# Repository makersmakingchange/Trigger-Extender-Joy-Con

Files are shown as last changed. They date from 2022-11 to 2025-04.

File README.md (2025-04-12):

# Trigger Extenders for Joy-Con Controller
The Trigger Extenders for Joy-Con Controllerr is an aid designed to make it easier to use the triggers and bumpers on the Nintendo Joy-Con controller.

Picture of Trigger Extender for Joy-Con.

## More info at
- [Makers Making Change Project Page](https://makersmakingchange.com/project/trigger-extender-joy-con/)

## How to Obtain a Trigger Extenders for Joy-Con
### 1. Do it Yourself (DIY) or Do it Together (DIT)

This is an open-source assistive technology, so anyone is free to build it. All of the files and instructions required to build the Trigger Extenders for Joy-Con are contained within this repository. Refer to the Maker Checklist below.

### 2. Request a build of this device

If you would like to obtain a Trigger Extenders for Joy-Con, you may submit a build request through the [MMC Library Page](https://makersmakingchange.com/project/trigger-extender-joy-con/). The requestor is responsible for the cost of materials and any shipping.

### 3. How to build this device for someone else

If you have the skills and equipment to build this device, and would like to donate your time to create it for someone who needs it, visit the [MMC Maker Wanted](https://makersmakingchange.com/maker-wanted/) section.

## Getting Started

### 1. Read the Makers Checklist

The Makers Checklist provides an overview of the steps required to build the device.

### 2. Print the 3D Printable components

Print the components. Refer to the 3D Printing Guide.

All of the files and individual print files can be in the [/Build_Files/3D_Printing_Files](/Build_Files/3D_Printing_Files/) folder.

### 3. Assemble the Trigger Extenders for Joy-Con

Reference the [Assembly Guide](/Documentation/Trigger_Extender_Joycon_Assembly_Guide_V1.0.pdf) for the tools and steps required to build each portion.

## Files
### Documentation
| Document             | Version | Link |
|----------------------|---------|------|
| Design Rationale     | 1.0     | [Trigger_Extender_Joycon_Design_Rationale](/Documentation/Trigger_Extender_Joycon_Design_Rationale_V1.0.pdf)     |
| Maker Checklist      | 1.0     | [Trigger_Extender_Joycon_Maker_Checklist](/Documentation/Trigger_Extender_Joycon_Maker_Checklist_V1.0.pdf)     |
| Bill of Materials    | 1.0     | [Trigger_Extender_Joycon_Bill_of_Materials](/Documentation/Trigger_Extender_Joycon_BOM_V1.0.xlsx)     |
| 3D Printing Guide    | 1.0     | [Trigger_Extender_Joycon_3D_Printing_Guide](/Documentation/Trigger_Extender_Joycon_3D_Printing_Guide_V1.0.pdf)     |
| Assembly Guide       | 1.0     | [Trigger_Extender_Joycon_Assembly_Guide](/Documentation/Trigger_Extender_Joycon_Assembly_Guide_V1.0.pdf)     |
| User Guide           | 1.0     | [Trigger_Extender_Joycon_User_Guide](/Documentation/Trigger_Extender_Joycon_User_Guide_V1.0.pdf)    |
| Changelog            | 1.0     | [Trigger_Extender_Joycon_Changelog](/Documentation/Trigger_Extender_Joycon_Changelog_V1.0.pdf)     |

### Build Files
 - [3D Printing Files](/Build_Files/3D_Printing_Files/)

## Attribution
Designer:
 - Sacha Potvin in the [GRRIT Program](https://albertahealthservices.ca/grh/Page14207.aspx) of the Glenrose Rehabilitation Hospital
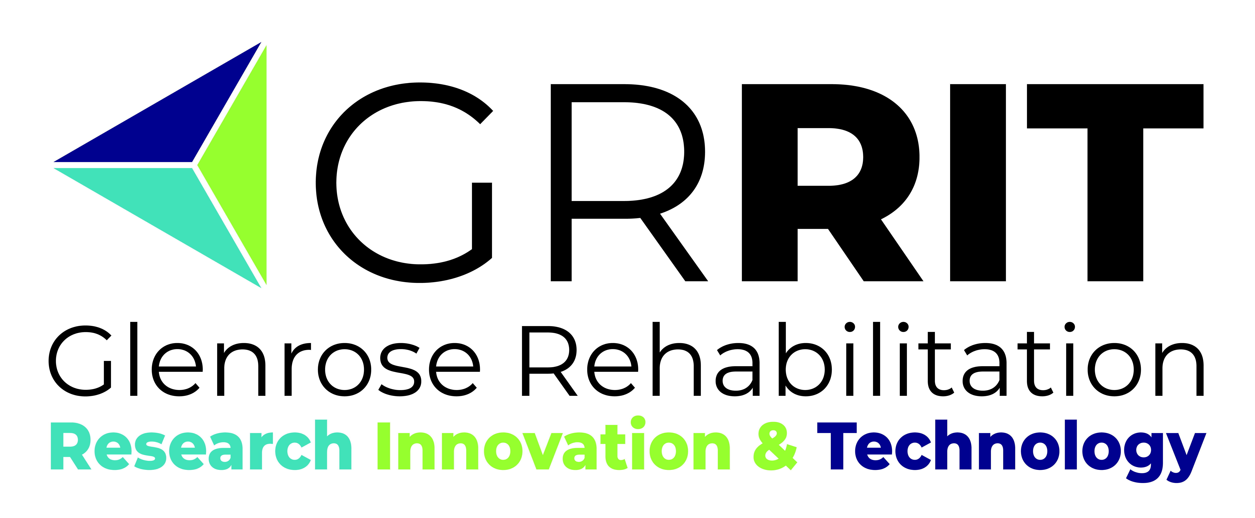
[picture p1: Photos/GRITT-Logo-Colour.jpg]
GRRIT Logo.


Documentation: 
 - Makers Making Change

## License
Everything needed or used to design, make, test, or prepare the Trigger Extenders for Joy-Con is licensed under the CERN 2.0 Permissive license <https://ohwr.org/project/cernohl/wikis/Documents/CERN-OHL-version-2> (CERN-OHL-P) . 

Accompanying material such as instruction manuals, videos, and other copyrightable works that are useful but not necessary to design, make, test, or prepare the Trigger Extenders for Joy-Con are published under a Creative Commons Attribution-ShareAlike 4.0 license https://creativecommons.org/licenses/by-sa/4.0/ (CC BY-SA 4.0).

---
<!-- ABOUT MMC START -->
## About Makers Making Change
[Makers Making Change Logo](https://www.makersmakingchange.com/)

Makers Making Change is a program of [Neil Squire](https://www.neilsquire.ca/), a Canadian non-profit that uses technology, knowledge, and passion to empower people with disabilities.

Makers Making Change leverages the capacity of community based Makers, Disability Professionals and Volunteers to develop and deliver affordable Open Source Assistive Technologies.

 - Website: [www.MakersMakingChange.com](https://www.makersmakingchange.com/)
 - GitHub: [makersmakingchange](https://github.com/makersmakingchange)
 - Bluesky: [@makersmakingchange.bsky.social](https://bsky.app/profile/makersmakingchange.bsky.social)
 - Instagram: [@makersmakingchange](https://www.instagram.com/makersmakingchange)
 - Facebook: [makersmakechange](https://www.facebook.com/makersmakechange)
 - LinkedIn: [Neil Squire Society](https://www.linkedin.com/company/neil-squire-society/)
 - Thingiverse: [makersmakingchange](https://www.thingiverse.com/makersmakingchange/about)
 - Printables: [MakersMakingChange](https://www.printables.com/@MakersMakingChange)

### Contact Us
For technical questions, to get involved, or to share your experience we encourage you to [visit our website](https://www.makersmakingchange.com/) or [contact us](https://www.makersmakingchange.com/s/contact).
<!-- ABOUT MMC END -->

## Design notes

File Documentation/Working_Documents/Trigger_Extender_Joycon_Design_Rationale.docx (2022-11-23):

# Introduction

The Trigger Extenders for Joy-Con Controller is designed to extend the shoulder bumpers and triggers on the Nintendo Joy-Con Controller to make it easier to activate them.

The device is intended for users that have issues using the shoulder bumpers and triggers on the Nintendo Joy-Con Controller.

# Research

No similar commercial or DIY products could be found.

# Requirements

## Goals

G01 | Extend the shoulder bumpers and triggers so they can be activated from more positions

## Functional Requirements

F01 | Device must extend the bumpers to be activated from more locations
F02 | Device must extend the triggers to be activated from more locations
F03 | Device must be easily attached and removed from the Nintendo Joy-Con Grip

## Constraints

C01 | Device must be entirely 3D printed

# Testing

The parts were printed, and the extenders were attached and removed from the slide-on trigger attachment 50 times to see if they would hold up over time. At the end of the testing the parts still work, although the attachments are slightly looser.

# Detailed Design

## Slide-on Trigger Attachment

~110x30x20mm

## Shoulder Trigger Extender

~160x35x5mm

## Shoulder Bumper Extender

~140x40x5mm

# Opportunities for Improvement

- The trigger extenders can break after repeatedly attaching and being removed from the trigger attachment. However, they need to be removed to take the Joy-Cons out to charge and use with the main switch body. Redesigning the extender so that it doesn’t block the insertion and removal of the Joy-Cons would extend the lifespan of this device.

© 2022 by Neil Squire. This work is licensed under the CC BY SA 4.0 License: http://creativecommons.org/licenses/by-sa/4.0 Files available at https://makersmakingchange.com/project/trigger-extender-joy-con/ Page 1 of 1

V1.0 | October 2022 Trigger Extenders for Joy-Con Controller Design Rationale

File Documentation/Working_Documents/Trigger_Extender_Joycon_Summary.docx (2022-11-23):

# Title

Trigger Extenders for Joy-Con Controller

## Subtitle

The Trigger Extender for Joy-Con Controller is an aid designed to make it easier to use the triggers and bumpers on the Nintendo Joy-Con Controller Grip.

## Device Details

### Overview

This 3D printed device attaches to the Nintendo Joy-Con Grip and extends the trigger and bumper buttons users to use the buttons more easily. The extenders allow for the bumper and trigger buttons to be activate from more positions.

### Usage

After assembling the device, the extenders can be pressed anywhere along their front to activate their respective button.

### Cost

~$0.50 for filament

### Build Instructions

To use this device, attach the central Slide-On Trigger Attachment to the centre of the Joy-Con Grip. Next insert the Joy-Cons to the Grip, then insert the trigger extenders in the lower clip and the bumper extenders in the upper clip.

#### Skills Required

- 3D Printing

#### Time Required

Printing time: 3h 1min

Assembly time: <5min

#### Tools

- 3D Printer

#### Components

- Slide-on Trigger Attachment
- Shoulder Trigger Extender
- Shoulder Bumper Extender

#### 3D Printing

All components can be printed with no support at 20% infill with a 0.2 layer height. All pieces can be printed using PLA filament.

### Attribution

Design: Sacha Potvin in the GRRIT Program (https://albertahealthservices.ca/grh/Page14207.aspx) of the Glenrose Rehabilitation Hospital

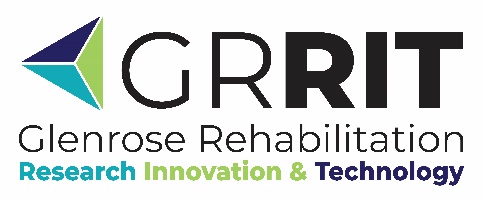
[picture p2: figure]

Documentation: Neil Squire / Makers Making Change

© 2022 by Neil Squire. This work is licensed under the CC BY SA 4.0 License: http://creativecommons.org/licenses/by-sa/4.0 Files available at https://makersmakingchange.com/project/trigger-extender-joy-con/ Page 1 of 2

V1.0 | October 2022 Trigger Extenders for Joy-Con Controller Summary

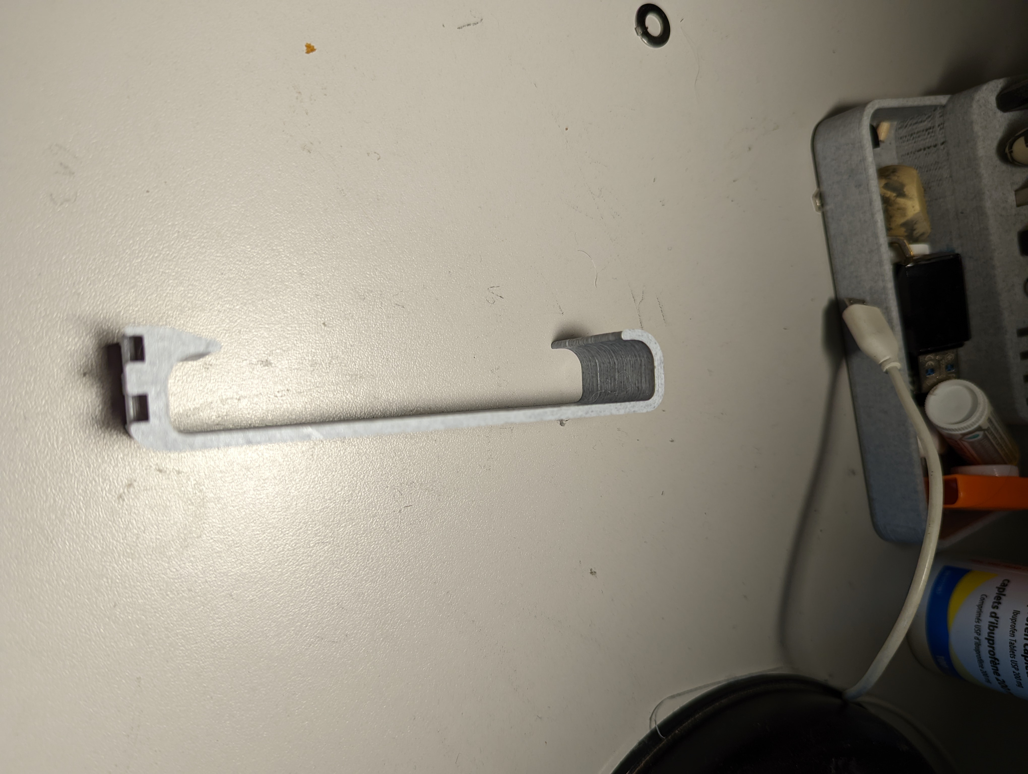
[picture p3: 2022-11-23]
Photos/Slide-On Trigger Attachment Side View.jpg

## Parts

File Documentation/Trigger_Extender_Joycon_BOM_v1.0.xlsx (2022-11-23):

Trigger Extenders for Joy-Con |  | Total Cost | Total Print time (hr) | Total filament (g)
Version: V1.0 | Last Updated: 2022-Nov-21 | $0.50 | 3.02 | 20
Commercial Parts:
Part type (Electrical. Mechanical, Sanitization, ect) | Part Name | Quantity Needed | Pkg Quantity | Price per package | Price per Unit | Price for qty needed | Link
N/A
3D Printed Parts ESTIMATED PRICING USING 1KG ROLL COST: | $25.00
Part | Description | Quantity Needed | TOTAL Mass (g) | Estimated Price | Print Time (Min) | Link
Slide-on Trigger Attachment | Attachment point for both extenders | 1 | 11 | $0.27 | 98
Shoulder Trigger Extender | Extender for the trigger buttons | 1 | 5 | $0.12 | 43
Shoulder Bumper Extender | Extender for the shoulder buttons | 1 | 4 | $0.10 | 40
 |  |  |  | $0.00
 |  |  |  | $0.00
 |  |  | Total Print Cost: | $0.50
Tools for Assembly
None required.
Alternatives (if there are other sources for some parts link them below)
Part and description | Link

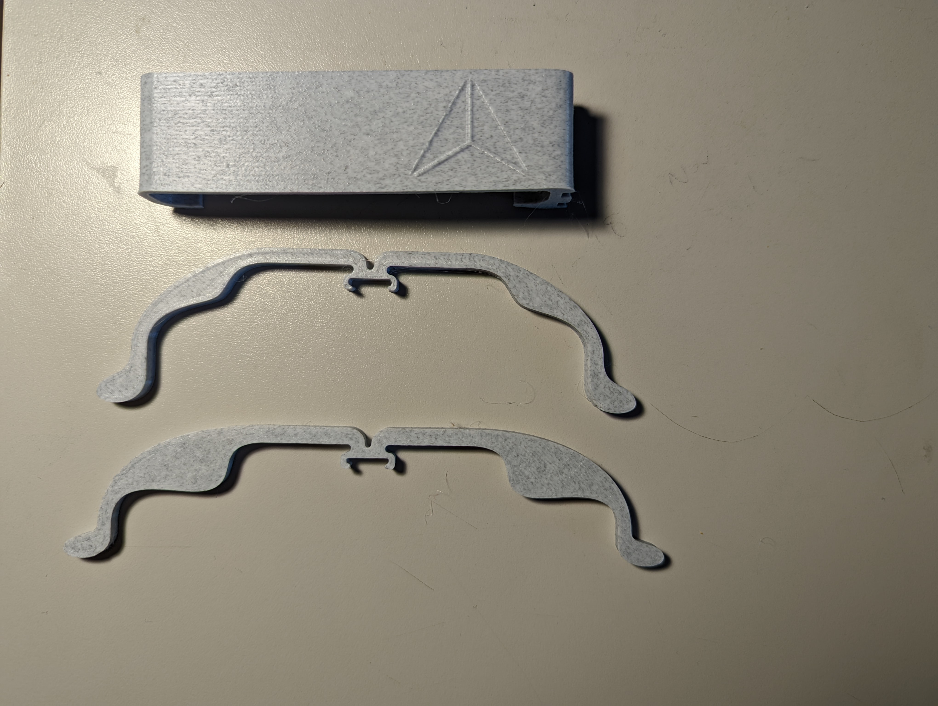
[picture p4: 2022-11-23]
Photos/All-Components-Top-View.jpg

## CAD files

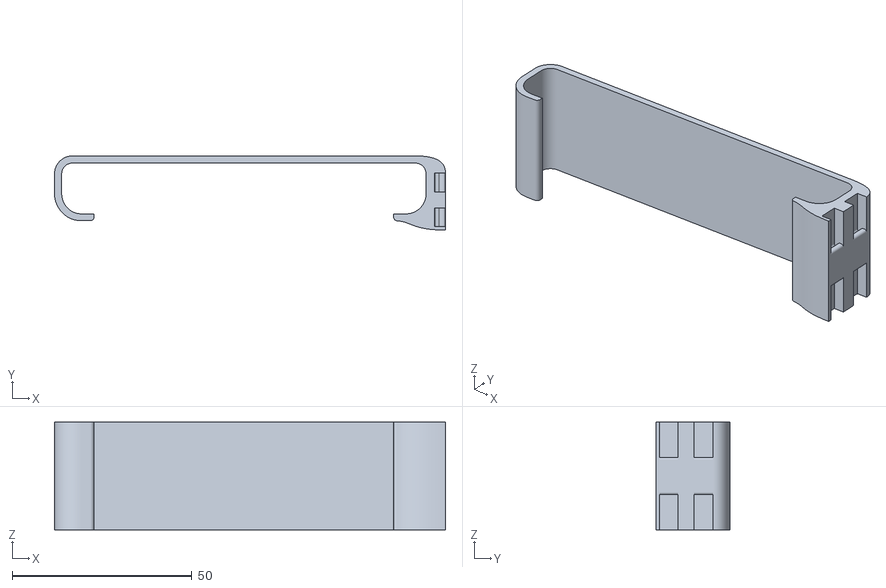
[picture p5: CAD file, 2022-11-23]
Build_Files/3D_Printing_Files/Slide-on Trigger Attachment.STL
108.6 x 20.6 x 30.0

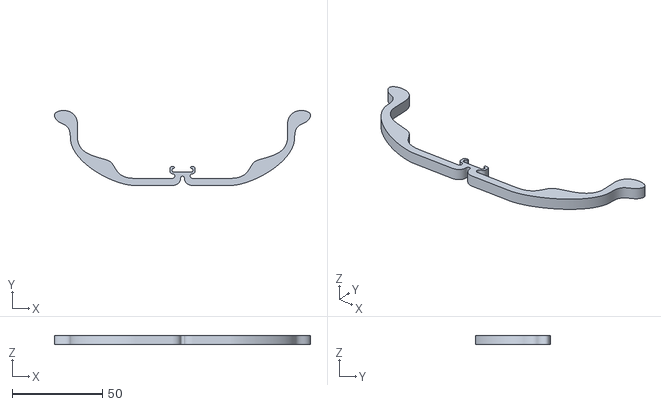
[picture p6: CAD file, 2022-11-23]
Build_Files/3D_Printing_Files/Shoulder Bumper Extender.STL
142.2 x 41.7 x 5.18

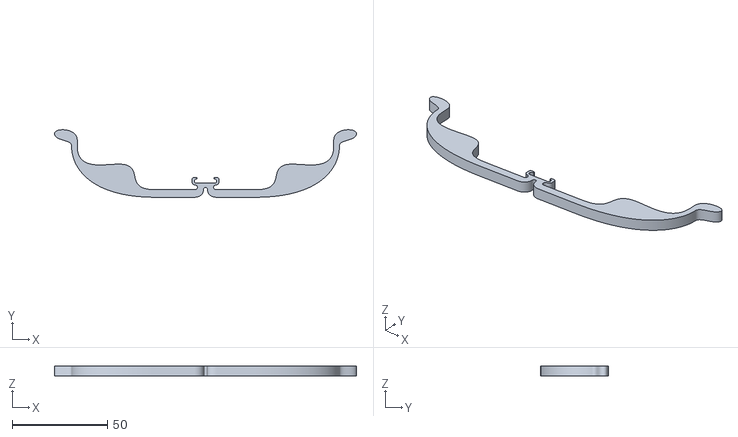
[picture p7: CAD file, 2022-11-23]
Build_Files/3D_Printing_Files/Shoulder Trigger Extender.STL
158.1 x 35.4 x 5.00

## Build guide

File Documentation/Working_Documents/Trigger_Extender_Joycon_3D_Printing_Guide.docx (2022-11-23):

# 3D Printing Summary

Metrics | V1.0
Total Print Time (min) | 181
Total Number of Components | 3
Typical Total Mass (g) | 20
Typical Number of Print Setups | 1

# 3D Printing Settings

Print File Name | Qty | Total Print Time (hr:min) | Mass (g) | Infill (%) | Support(Y/N) | Layer Height/ Nozzle Diameter(mm) | Notes (orientation, special settings, etc.)
Slide-on Trigger Attachment.stl | 1 | 1:38 | 11 | 20 | N | 0.2/0.4 | - Print in default STL orientation
Shoulder Trigger Extender.stl | 1 | 0:43 | 5 | 20 | N | 0.2/0.4 | - Print in default STL orientation
Shoulder Bumper Extender.stl | 1 | 0:40 | 4 | 20 | N | 0.2/0.4 | - Print in default STL orientation

# Customization Options

- Any of the 3 parts can be printed in separate colours to customize the Trigger Extenders

# Post-Processing

- Any sharp edges should be sanded down/filed off.

# Examples of Quality Prints

Photos of Slide-on Trigger Attachment.stl

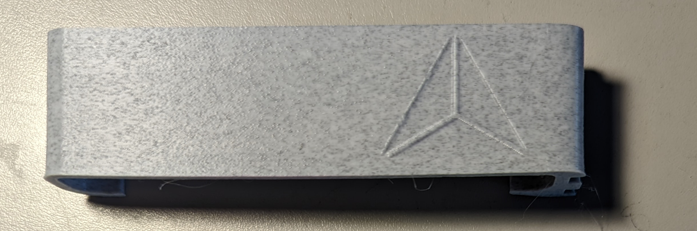
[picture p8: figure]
Trigger Attachment top view
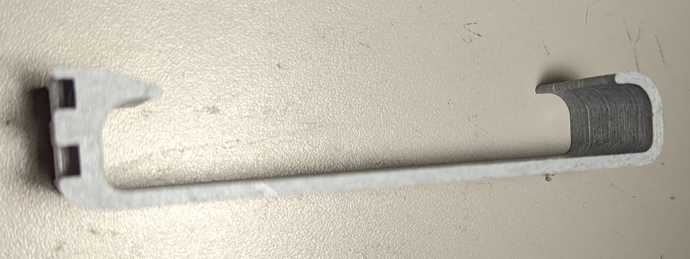
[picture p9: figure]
Trigger Attachment side view

Photos of Shoulder Trigger Extender.stl

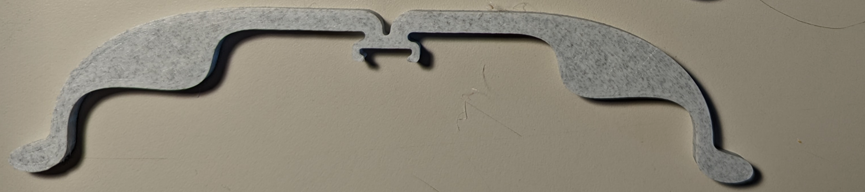
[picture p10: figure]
Trigger Extender top view

Photos of Shoulder Bumper Extender.stl

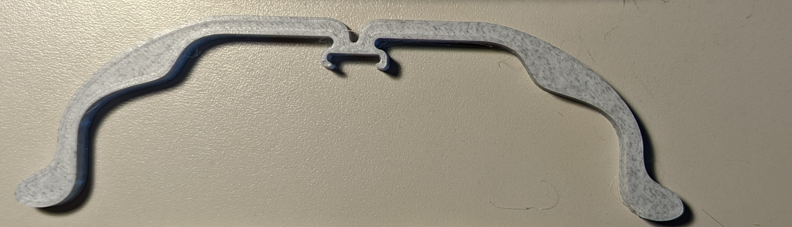
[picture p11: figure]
Bumper Extender top view

© 2022 by Neil Squire. This work is licensed under the CC BY SA 4.0 License: http://creativecommons.org/licenses/by-sa/4.0 Files available at https://makersmakingchange.com/project/trigger-extender-joy-con/ Page 1 of 2

V1.0 | October 2022 Trigger Extenders for Joy-Con Controller 3D Printing Guide

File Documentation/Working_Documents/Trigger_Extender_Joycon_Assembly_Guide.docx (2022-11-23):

# Required Components

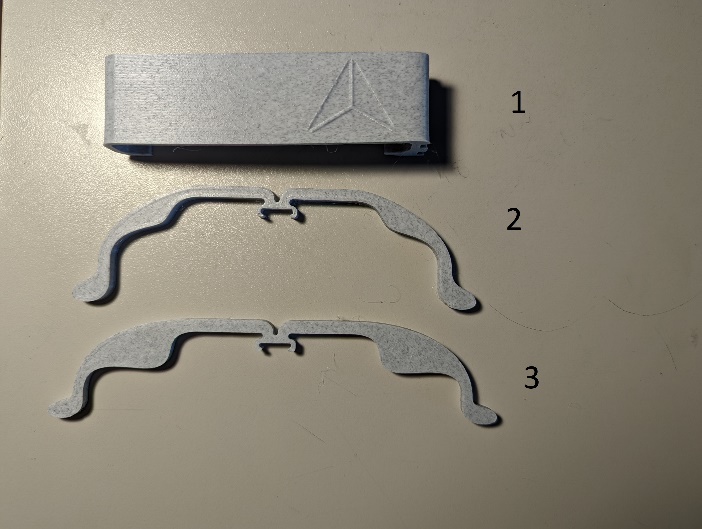
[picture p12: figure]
Three 3D printed parts, labeled 1-3 from top to bottom

| BOM 1. Slide-on Trigger Attachment 2. Shoulder Bumper Extender 3. Shoulder Trigger Extender

# Required Tools

- Sandpaper
- Hobby knife

# Assembly Instructions

## Step 1

Slide the trigger attachment over the centre section of the Joy-Con holder

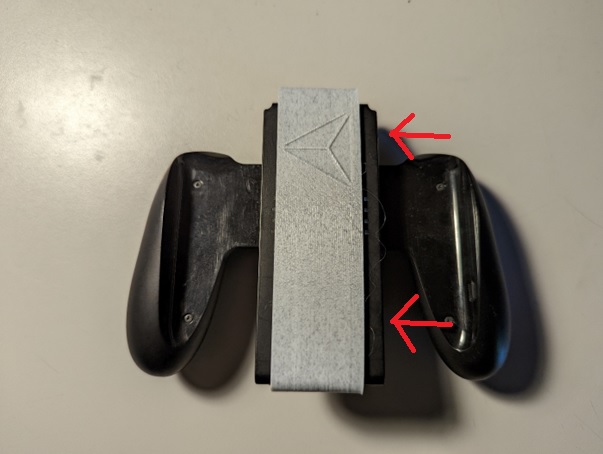
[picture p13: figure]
Nintendo Joy-Con Grip with Slide-On Trigger Attachment. Arrows show what direction it slides on from.

## Step 2

Insert both Joy-Cons into the holder.

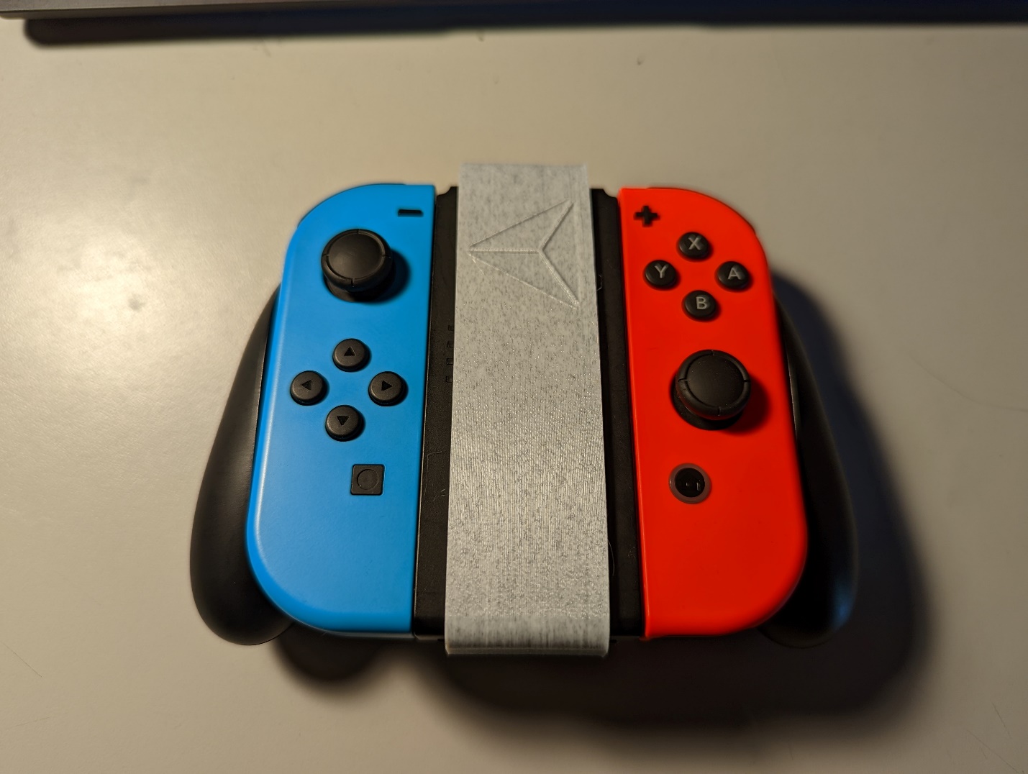
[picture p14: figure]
Assembly from previous step with both joycons now inserted

## Step 3

Clip the trigger extender onto the bottom slot of the trigger attachment

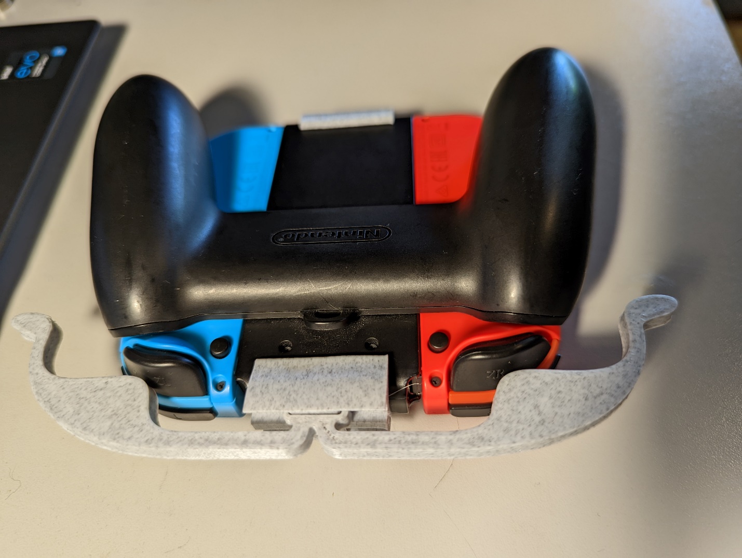
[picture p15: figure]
Previous assembly flipped upside down, with the trigger extender attached to the bottom slot

## Step 4

Attach the bumper extender to the top slot of the trigger attachment

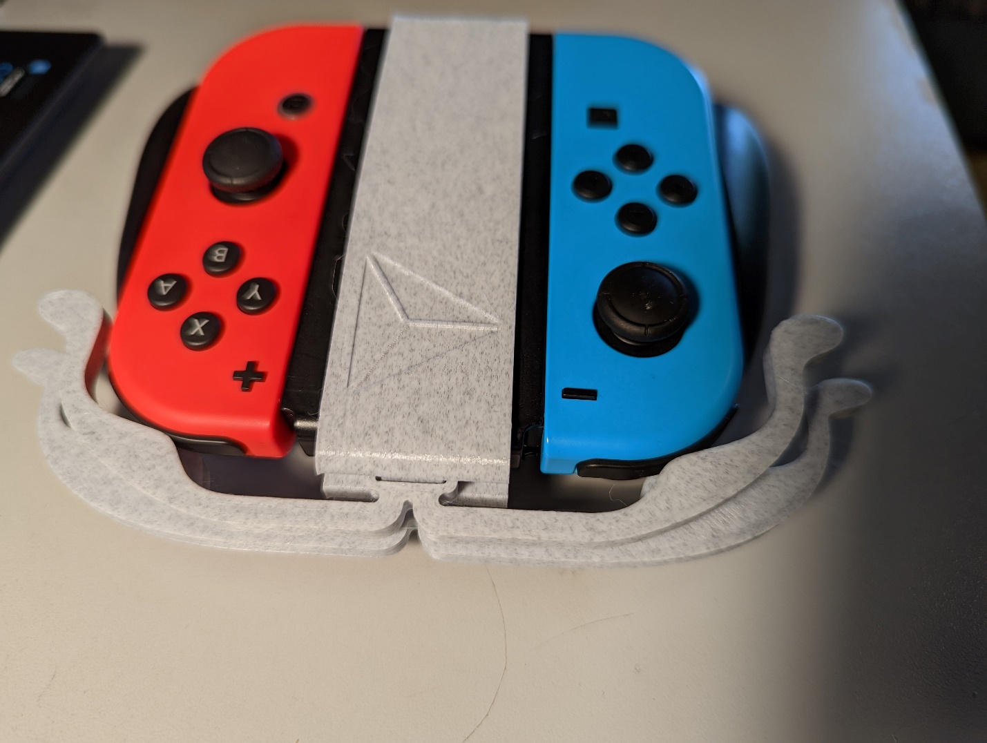
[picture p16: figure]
Assembly right-side up, with bumper extender attached to the top slot

© 2022 by Neil Squire. This work is licensed under the CC BY SA 4.0 License: http://creativecommons.org/licenses/by-sa/4.0 Files available at https://makersmakingchange.com/project/trigger-extender-joy-con/ Page 1 of 1

V1.0 | October 2022 Trigger Extenders for Joy-Con Controller Assembly Guide

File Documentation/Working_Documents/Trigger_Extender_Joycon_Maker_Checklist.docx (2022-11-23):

# Maker To Do List

- Read through the Assembly Guide to become familiar with required components, tools, supplies, and safety gear and overall assembly steps.
- Talk to User about customization options (e.g., color, any special requests, etc.)
- Gather tools, supplies, and safety equipment.
- Print the device
- Test device
- Print “User Quick Guide”

# Items to Give to User

- Assembled, tested device
- “User Quick Guide”

© 2022 by Neil Squire. This work is licensed under the CC BY SA 4.0 License: http://creativecommons.org/licenses/by-sa/4.0 Files available at https://makersmakingchange.com/project/trigger-extender-joy-con Page 1 of 1

V1.0 | October 2022 Trigger Extender for Joy-Con Controller Maker Checklist

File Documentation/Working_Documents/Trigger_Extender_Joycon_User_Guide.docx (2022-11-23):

## Introduction

The Trigger Extender for Joy-Con Controller is an aid designed to make it easier to use the triggers and bumpers on the Nintendo Joy-Con Grip

## Features

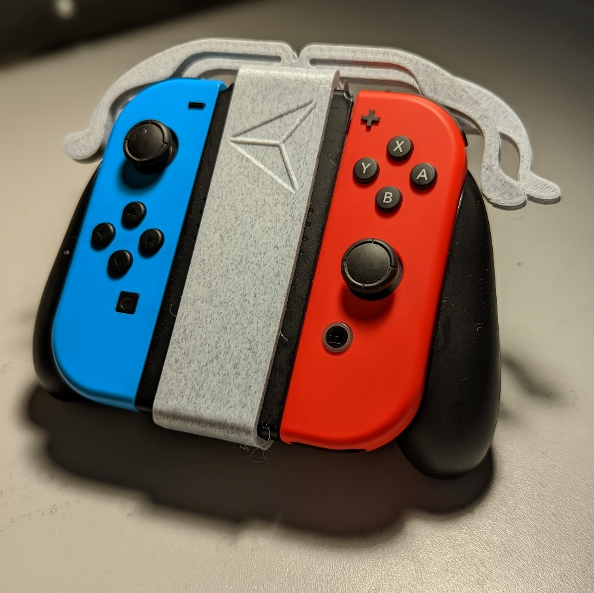
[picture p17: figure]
Nintendo Joy-Con Grip with Trigger Extender attached

## Usage

Once the device is assembled as per the Assembly Guide, pressing on the bumper and trigger extensions will press the respective bumper and trigger buttons.

## Compatibility

This device is designed to connect to the official Nintendo Joy-Con Grip.

## Specifications

The completed assembly weighs approximately 20 grams

## Cleaning

The device can be wiped clean with a damp cloth.

© 2022 by Neil Squire. This work is licensed under the CC BY SA 4.0 License: http://creativecommons.org/licenses/by-sa/4.0 Files available at https://makersmakingchange.com/project/trigger-extender-joy-con/ Page 2 of 3

V1.0 | October 2022 Trigger Extender for Joy-Con Controller user Quick Guide

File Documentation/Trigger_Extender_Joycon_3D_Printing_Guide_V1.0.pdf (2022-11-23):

V1.0 | October 2022

## Trigger Extenders for Joy-Con Controller

## 3D PRINTING GUIDE

© 2022 by Neil Squire. (https://neilsquire.ca/)
This work is licensed under the CC BY SA 4.0 License: http://creativecommons.org/licenses/by-sa/4.0 Files available at https://makersmakingchange.com/project/trigger-extender-joy-con/

### 3D Printing Summary

Metrics | V1.0
Total Print Time (min) | 181
Total Number of Components | 3
Typical Total Mass (g) | 20
Typical Number of Print Setups | 1

### 3D Printing Settings

Print File Name | Qty | Total Print Time (hr:min) | Mass (g) | Infill (%) | Support(Y/N) | Layer Height/ Nozzle Diameter(mm) | Notes (orientation, special settings, etc.)
Slide-on Trigger Attachment.stl | 1 | 1:38 | 11 | 20 | N | 0.2/0.4 | -Print in default STL orientation
Shoulder Trigger Extender.stl | 1 | 0:43 | 5 | 20 | N | 0.2/0.4 | -Print in default STL orientation
Shoulder Bumper Extender.stl | 1 | 0:40 | 4 | 20 | N | 0.2/0.4 | -Print in default STL orientation

### Customization Options

- Any of the 3 parts can be printed in separate colours to customize the Trigger Extenders

### Post-Processing

- Any sharp edges should be sanded down/filed off.

## 3D PRINTING GUIDE

### Examples of Quality Prints

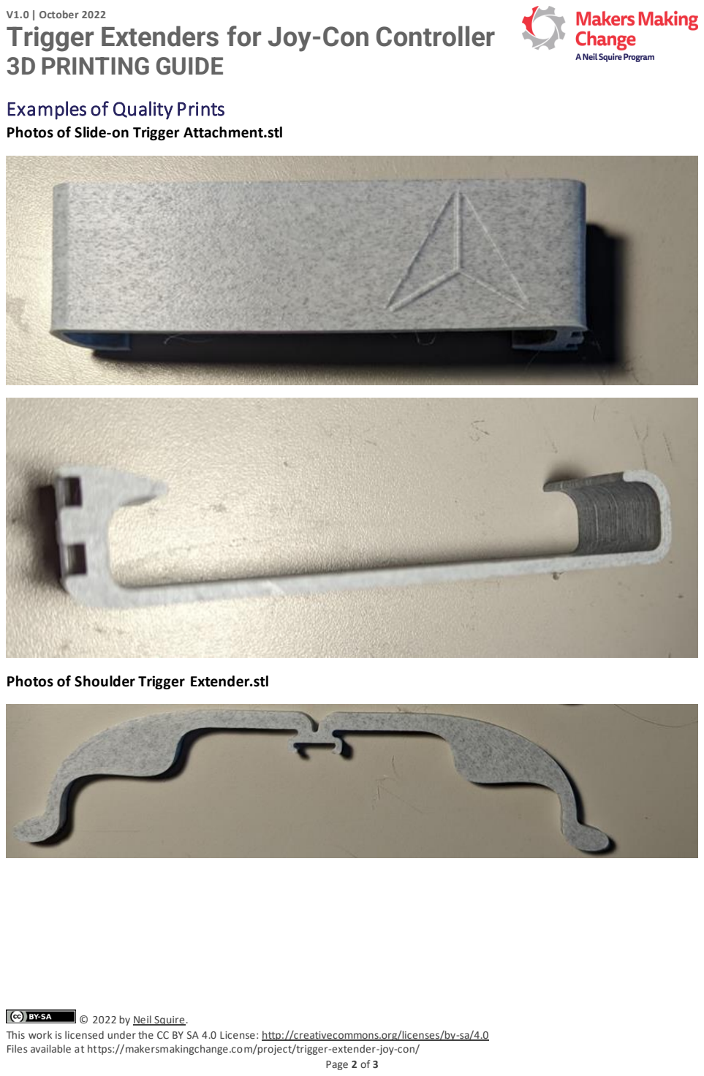
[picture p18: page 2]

© 2022 by Neil Squire. (https://neilsquire.ca/)

Photos of Slide-on Trigger Attachment.stl

Photos of Shoulder Trigger Extender.stl

## 3D PRINTING GUIDE

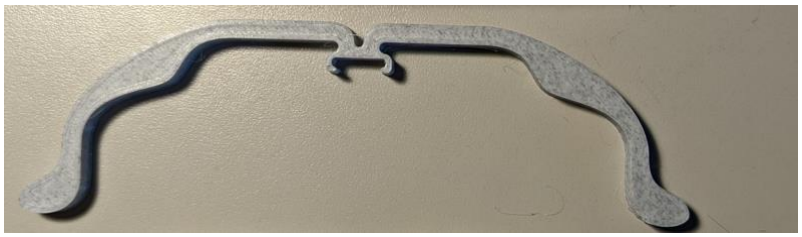
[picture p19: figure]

© 2022 by Neil Squire. (https://neilsquire.ca/)

Photos of Shoulder Bumper Extender.stl

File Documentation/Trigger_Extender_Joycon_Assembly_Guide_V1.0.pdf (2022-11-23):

V1.0 | October 2022

# Trigger Extenders for Joy-Con Controller

# ASSEMBLY GUIDE

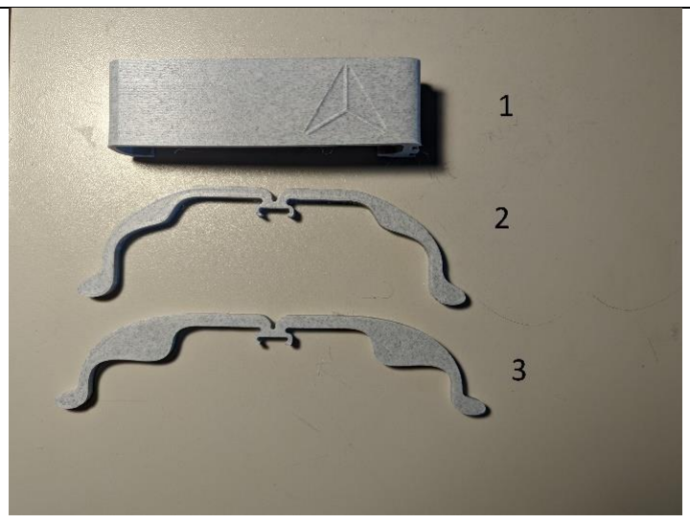
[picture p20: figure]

© 2022 by Neil Squire. (https://neilsquire.ca/)
This work is licensed under the CC BY SA 4.0 License: http://creativecommons.org/licenses/by-sa/4.0 Files available at https://makersmakingchange.com/project/trigger-extender-joy-con/

# Required Components

## BOM 1. Slide-on Trigger Attachment 2. Shoulder Bumper Extender 3. Shoulder Trigger Extender

# Required Tools

## - Sandpaper - Hobby knife

# ASSEMBLY GUIDE

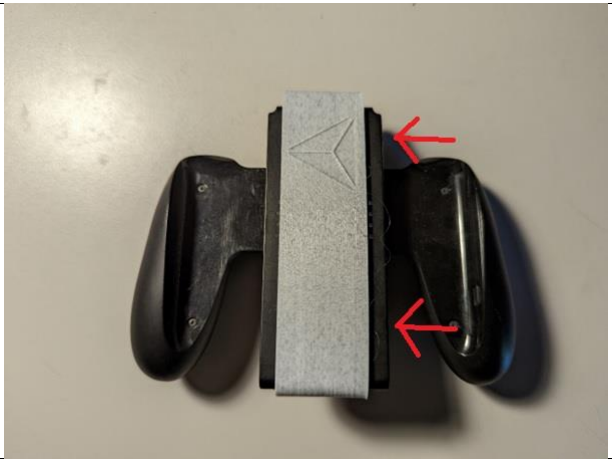
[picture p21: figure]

© 2022 by Neil Squire. (https://neilsquire.ca/)

# Assembly Instructions

## Step 1

## Slide the trigger attachment over the centre section of the Joy-Con holder

# ASSEMBLY GUIDE

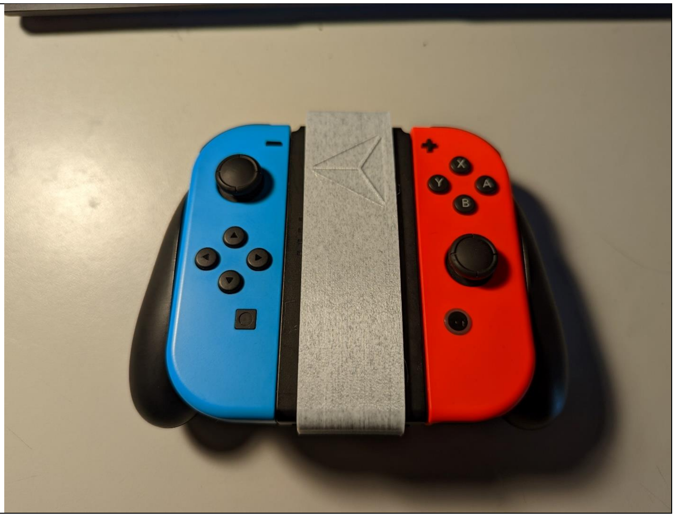
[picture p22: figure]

© 2022 by Neil Squire. (https://neilsquire.ca/)

## Step 2

Insert both Joy-Cons into the holder.

# ASSEMBLY GUIDE

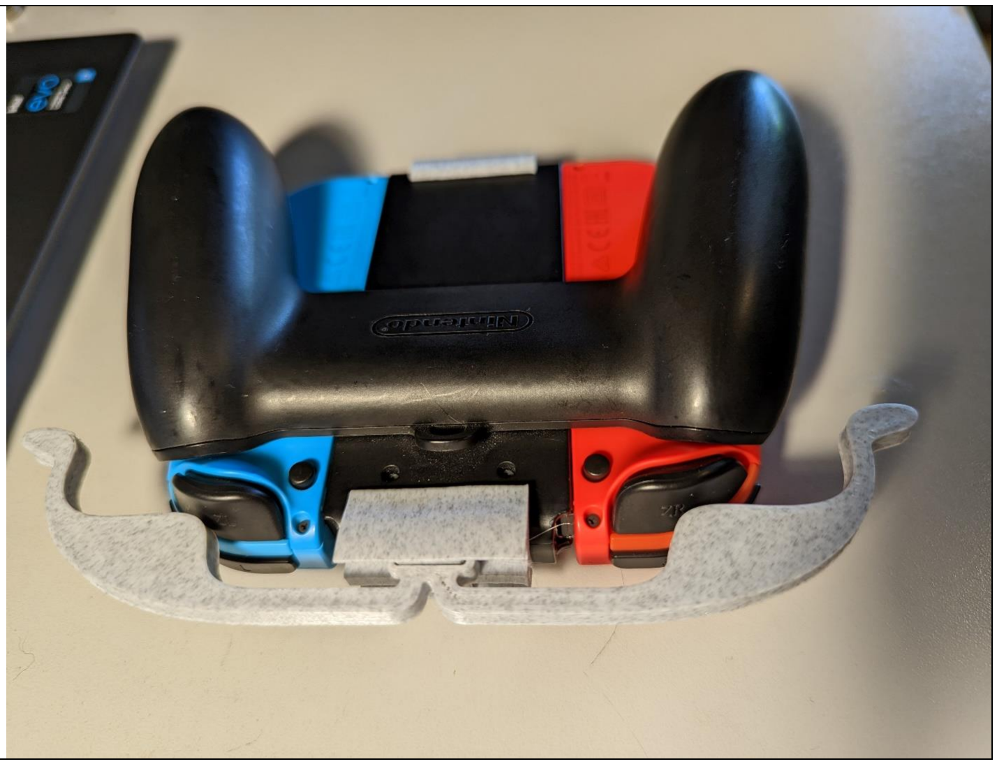
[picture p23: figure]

© 2022 by Neil Squire. (https://neilsquire.ca/)

## Step 3

## Clip the trigger extender onto the bottom slot of the trigger attachment

# ASSEMBLY GUIDE

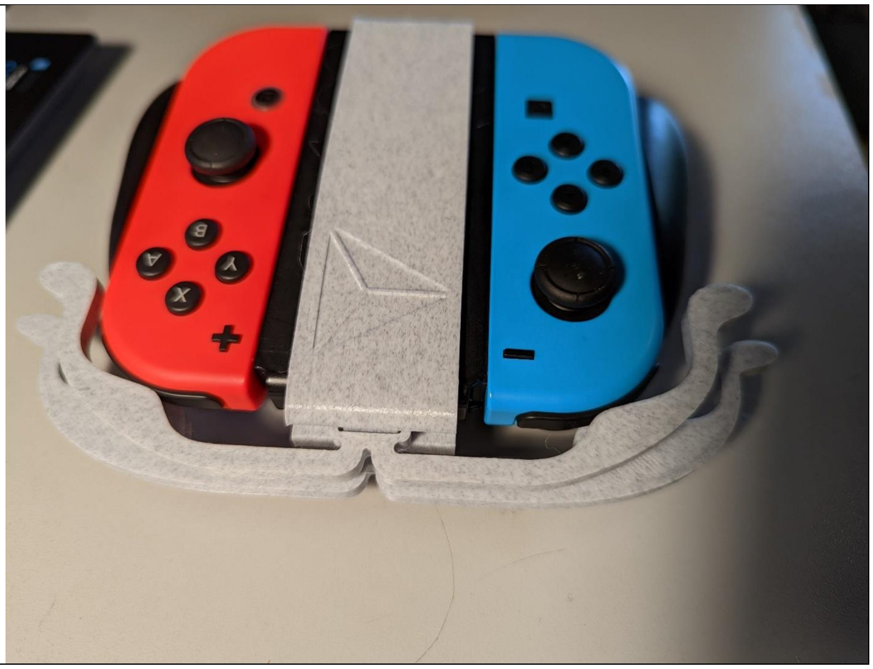
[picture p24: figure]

© 2022 by Neil Squire. (https://neilsquire.ca/)

## Step 4

## Attach the bumper extender to the top slot of the trigger attachment

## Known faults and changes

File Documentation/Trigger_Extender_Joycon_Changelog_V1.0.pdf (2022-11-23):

V1.0| October 2022

# Trigger Extenders for Joy-Con Controller

# CHANGELOG

© 2022 by Neil Squire. (https://neilsquire.ca/)
This work is licensed under the CC BY SA 4.0 License: http://creativecommons.org/licenses/by-sa/4.0 Files available at https://makersmakingchange.com/project/trigger-extender-joy-con/

# Version 1.0 | 2022-Oct-26

- Design by Sacha Potvin in the GRRIT Program (https://albertahealthservices.ca/grh/Page14207.aspx) of the Glenrose Rehabilitation Hospital

## - Documentation by Neil Squire / Makers Making Change
